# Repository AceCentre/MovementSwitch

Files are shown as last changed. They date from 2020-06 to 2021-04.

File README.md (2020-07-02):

# MovementSwitch

> Hardware project to make a very sensitive, self calibrating and auto-adjusting on-body switch

MovementSwitch is a Arduino project designed to work with a range of Arduino boards (e.g. Arduino Pro micro) and a GY-521 Gyroscope. The device self calibrates to a users movement and a potentiometer can be used to adjust the sensitivity. 



## Bill of materials

* x1 [Arduino Pro Micro](https://store.arduino.cc/arduino-micro)
* x1 [Gy-521 Gyroscope-Accelerometer](https://www.amazon.co.uk/WayinTop-MPU-6050-Gyroscope-Accelerometer-Converter/dp/B07P5YXBXV/)
* x1 [10K Pot](https://shop.pimoroni.com/products/pt10lv-horizontal-trimmer-multiple-values)
* x1 [Momentary Pushbutton or switch](https://shop.pimoroni.com/products/momentary-pushbutton-switch-12mm-square)

## Arduino wiring

* **Pin** 4 - Switch/Pushbutton **State**: Active Low 
* **Pin** A0 - Potentiometer	**State**: Active Low 
* **Pin** 5 - Switch Output/Relay	**State**: Active Low 
* **Pin** 3 -  SCL of GY-521
* **Pin** 2 -  SDA of GY-521
* **Pin** 7 -  INT of GY-521
* **Pin** 9 -  Neopixel

See also this [TinyCad Diagram](https://github.com/AceCentre/MovementSwitch/blob/master/MovementSwitchSCM.dsn) :

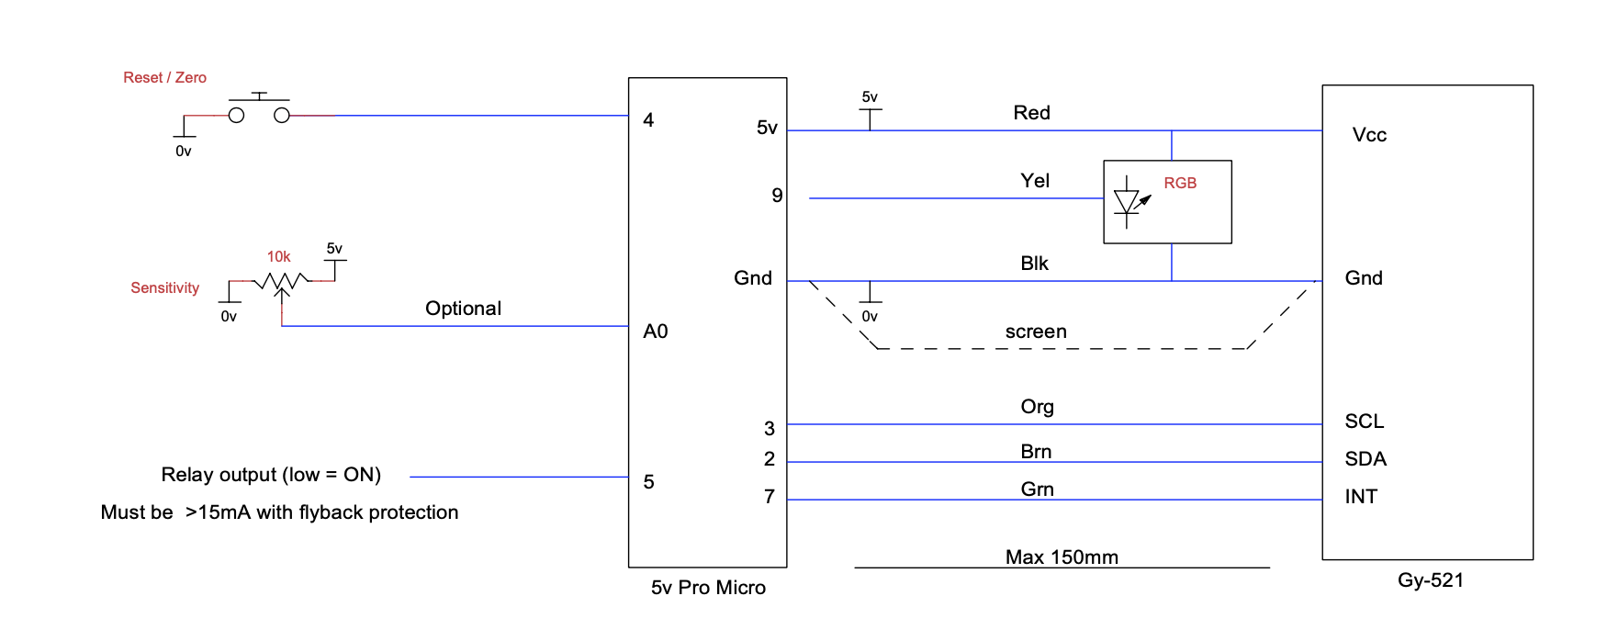
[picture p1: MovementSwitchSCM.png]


### Usage

Wire it all up. The neopixel displays different colours:

* **RED**: On first start for a few seconds as device calibrates. Wait with steady hand until complete
* **White**: OFF. Waiting to detect movement down* (up is an option)
* **Green**: ON A single keyboard character* will have been sent to the PC Now waiting to detect movement up*
* **Yellow**: OFF. Indicates that the user has managed to return further than original OFF position by a factor of 2. Consider reducing Sensitivity

**Zero / Reset Button:**

On press a fast zero will occur and the led will be Purple for a second or less then return to White indicating OFF

If the unit has had a major movement (dropped etc) and a quick reset is not possible, then the display will colour Red and commence a full reset taking a few seconds in the same manner as starting up.

**Sensitivity Knob:**

Max sensitivity when fully clockwise

## Contributing
Pull requests are welcome. For major changes, please open an issue first to discuss what you would like to change.

## Files

All the Arduino code is in the sub-directory **MovementSwitch**

* MovementSwitch.ino - Main source code file
* A_Main.ino - Main Gyro State Machine
* B_Gyro_.ino - Gyro Read data functions
* F_MonitorLight.ino - Logging functions. "Light" because it is a lightweight version of a more complex version Graham uses in his projects

### Required libraries 

You will need **THREE** libraries in your Arduino library folder for this to work:

* [I2Cdevlib](https://github.com/jrowberg/i2cdevlib/tree/master/Arduino/I2Cdev) and the [I2Cdevlib-MPU6050](https://github.com/jrowberg/i2cdevlib/tree/master/Arduino/MPU6050) Library in your Library folder. 
* [Adafruit Neopixel](https://github.com/adafruit/Adafruit_NeoPixel) Library

## Documentation Development

We use [vuepress](http://vuepress.vuejs.org) for documentation 

```bash
yarn dev
yarn build
```

## Credits

* Graham Law - Check out <http://celticmagic.org> for some great AT hardware. Graham wrote *ALL* of this code. Graham is a legend. Hire him! [See his page here which documents it from his side](https://www.celticmagic.org/movement-detector). 
* Gerard Cullen <http://www.rhn.org.uk> - Original inspiration and version 1 of this project was down to Gerard

## License
[MIT](https://choosealicense.com/licenses/mit/)

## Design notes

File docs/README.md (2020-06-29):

---
home: true
heroImage: https://v1.vuepress.vuejs.org/hero.png
tagline: Hardware project to make a very sensitive, self calibrating and auto-adjusting on-body switch
actionText: Quick Start →
actionLink: /guide/
features:
- title: Feature 1 Title
  details: Feature 1 Description
- title: Feature 2 Title
  details: Feature 2 Description
- title: Feature 3 Title
  details: Feature 3 Description
footer: Made by Will Wade with ❤️
---

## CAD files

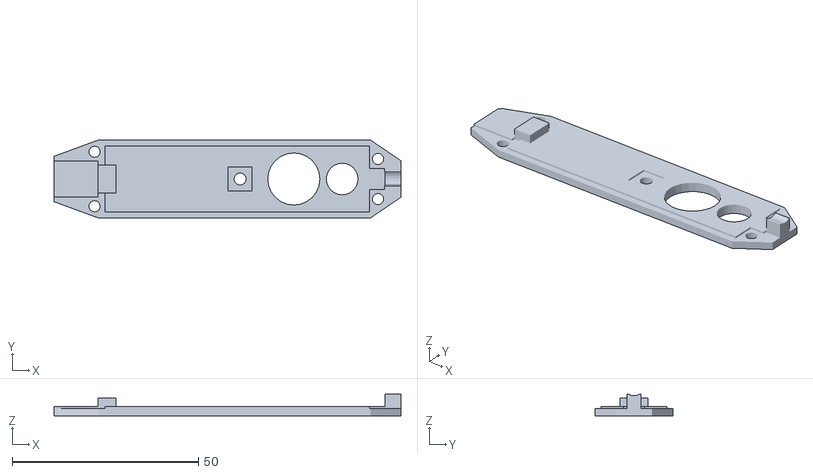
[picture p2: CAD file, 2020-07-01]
hardware/3D printing/ACE CoffinLid.stl
93.2 x 21.0 x 5.82

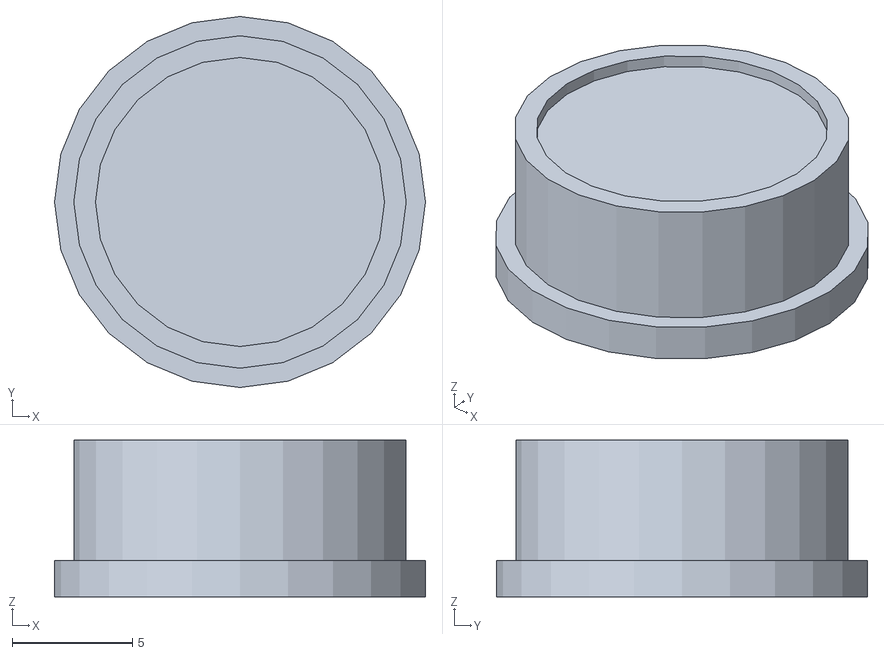
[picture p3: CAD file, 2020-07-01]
hardware/3D printing/ACE CoffinButton.stl
15.4 x 15.4 x 6.50

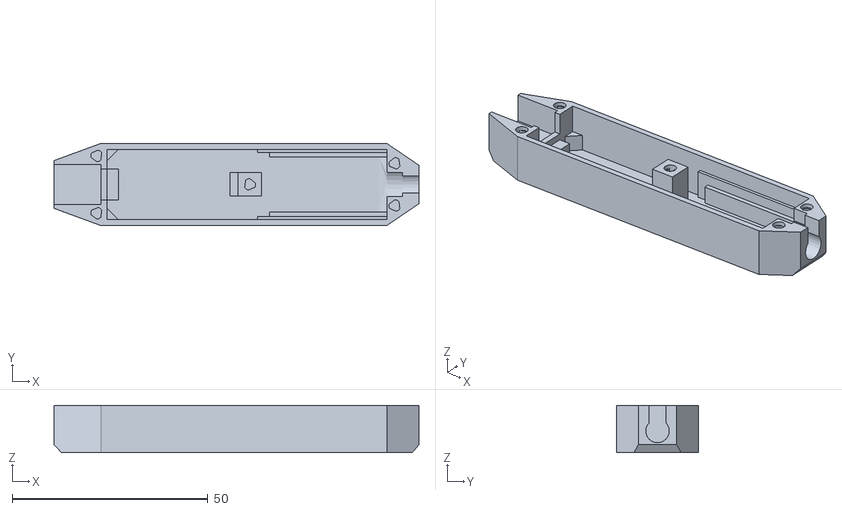
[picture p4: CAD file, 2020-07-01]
hardware/3D printing/ACE CoffinCase.stl
93.2 x 21.0 x 12.0

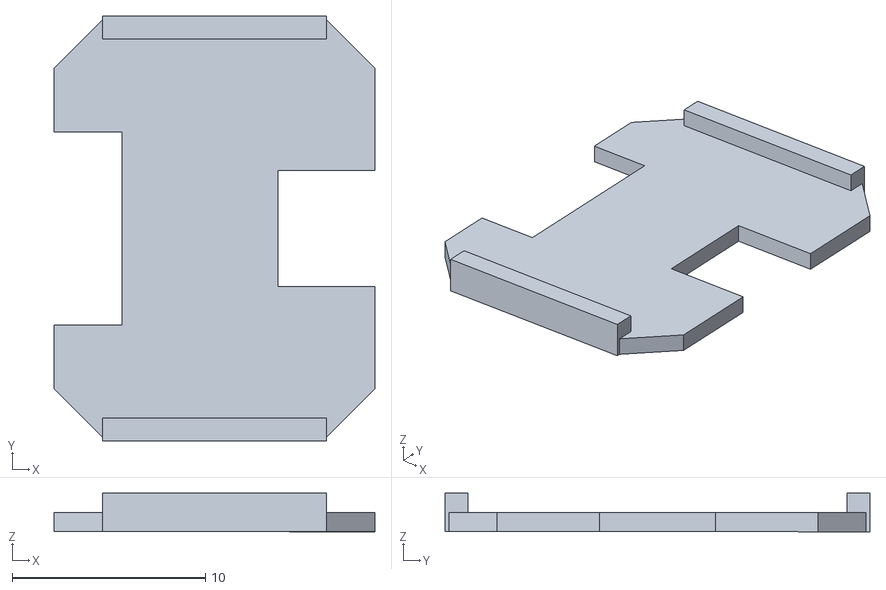
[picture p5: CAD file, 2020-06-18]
hardware/3D printing/ACE spacer.stl
16.6 x 22.0 x 2.00

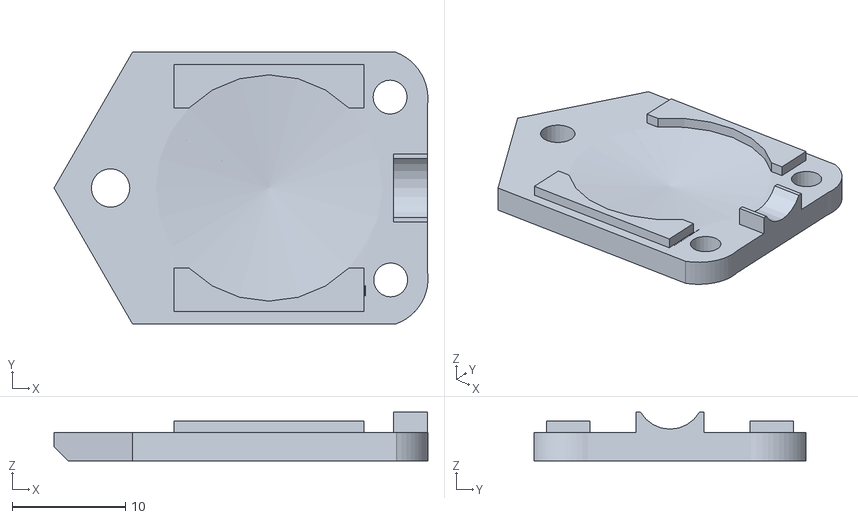
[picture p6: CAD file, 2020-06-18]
hardware/3D printing/ACE lens.stl
33.1 x 24.0 x 4.30

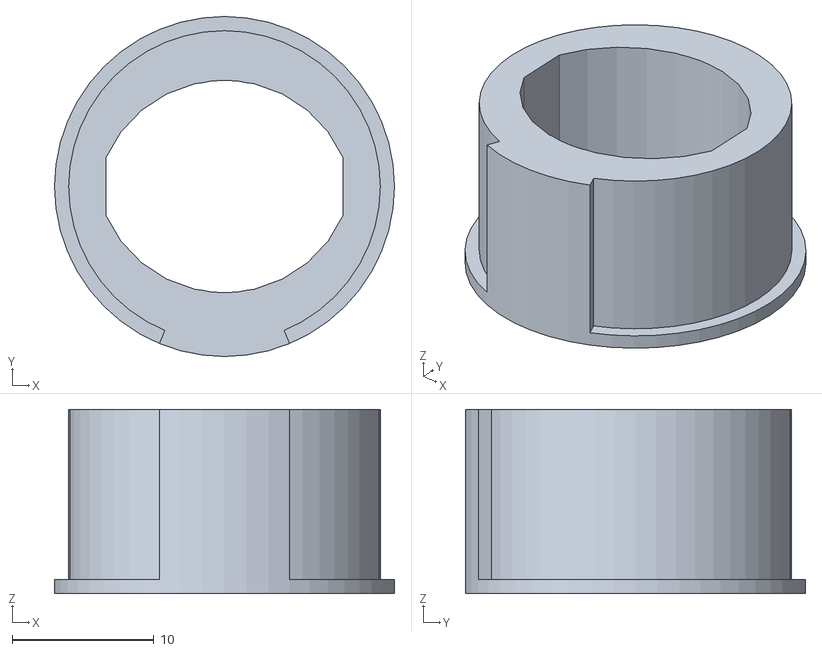
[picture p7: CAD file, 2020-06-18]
hardware/3D printing/ACE finger adaptor M .stl
24.0 x 24.0 x 13.0

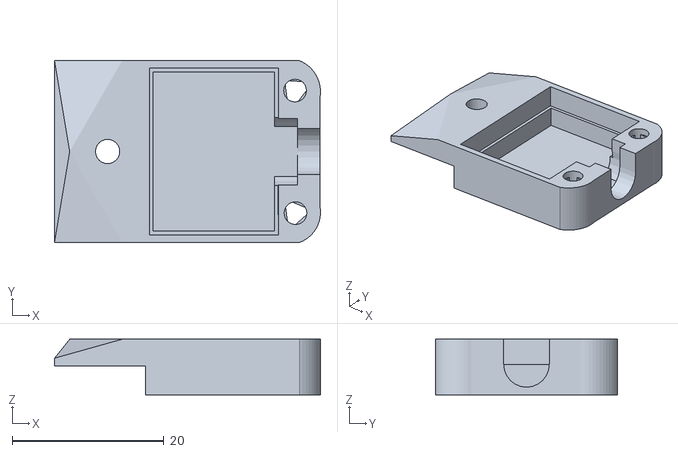
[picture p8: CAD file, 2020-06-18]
hardware/3D printing/ACE Case.stl
35.1 x 24.0 x 7.32

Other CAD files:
hardware/3D printing/ACE finger adaptor.stl
hardware/3D printing/ACE finger adaptor L .stl
hardware/3D printing/ACE finger adaptor S.stl
hardware/3D printing/ACE Case.skp

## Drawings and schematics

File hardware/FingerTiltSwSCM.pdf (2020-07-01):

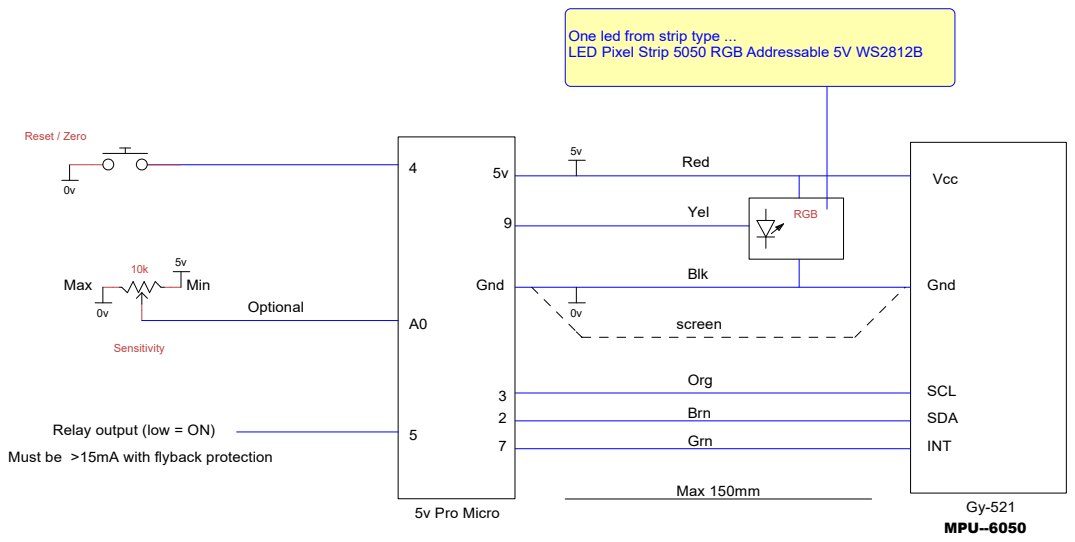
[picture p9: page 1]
Gnd; Vcc; 7 INT; SCL; 2 SDA; 5v Pro Micro; Sensitivity; RGB; Optional; Grn; Brn; Org; Red; Blk; Yel; Reset / Zero Relay output (low = ON); screen Max 150mm; MPU--6050; Max; Min

One led from strip type ...
LED Pixel Strip 5050 RGB Addressable 5V WS2812B

Must be >15mA with flyback protection

Title
Finger tilt switch
Author
GCL
Celtic Magic

File D:\Google Drive Stora ... FingerTiltSwSCM.dsn | Document SCM20052

Revision 0.1 | Date 15/6/20 | Sheets 1

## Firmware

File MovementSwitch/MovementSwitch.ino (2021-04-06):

     /*
Version:      1.2  29/7/20

1.2   FIXED  2D not reliably recalled after power up if in User mode


Open Source License - please leave this header intact.

Project:      Movement Detector based on the MPU650 Gyro
Originator:   Celtic Magic     www.celticmagic.org
Sponsored by: ACE Centre UK

Credits:
Thanks and credit given to Gyro  Libraries from Jeff Rowberg & the Arduino community.
Based on InvenSense MPU-6050 register map document rev. 2.0, 5/19/2011 (RM-MPU-6000A-00)
8/24/2011 by Jeff Rowberg <jeff@rowberg.net>

Legal bit:
THIS SOFTWARE IS PROVIDED BY THE COPYRIGHT HOLDERS AND CONTRIBUTORS "AS IS"
AND ANY EXPRESS OR IMPLIED WARRANTIES, INCLUDING, BUT NOT LIMITED TO, THE
IMPLIED WARRANTIES OF MERCHANTABILITY AND FITNESS FOR A PARTICULAR PURPOSE
ARE DISCLAIMED. IN NO EVENT SHALL THE COPYRIGHT HOLDER OR CONTRIBUTORS BE
LIABLE FOR ANY DIRECT, INDIRECT, INCIDENTAL, SPECIAL, EXEMPLARY, OR
CONSEQUENTIAL DAMAGES (INCLUDING, BUT NOT LIMITED TO, PROCUREMENT OF
SUBSTITUTE GOODS OR SERVICES; LOSS OF USE, DATA, OR PROFITS; OR BUSINESS
INTERRUPTION) HOWEVER CAUSED AND ON ANY THEORY OF LIABILITY, WHETHER IN
CONTRACT, STRICT LIABILITY, OR TORT (INCLUDING NEGLIGENCE OR OTHERWISE)
ARISING IN ANY WAY OUT OF THE USE OF THIS SOFTWARE, EVEN IF ADVISED OF THE    
POSSIBILITY OF SUCH DAMAGE.
*/   

//*******************************************************************************************************************
//***************  User Config      *********************************************************************************   
//*******************************************************************************************************************

  #define  DETECTION_STYLE_USER                      // _USER  Manual select 2D or 3D  
                                                     // _2D   fixed-  2D tilt normal    
                                                     // _2DR  fixed-  2D tilt reverse 
                                                     // _3D   fixed-  free space detection  
                                               
  #define  KEY_CHAR                      ' '         // Keyboard charecter when pressed - enter ASCII number for charector eg 97 = a     or enclose for same result ie 'a'      32 = Space
  #define  SENSITIVITY                     0         // 1-1000     if set to zero then sensitivity pot used from pin AD0
  #define  AUTO_CENTRE_RATE              0.2         // 0.1 - 1.0  this is how strong the auto centering works 
  

  #define  OVER_TRAVEL_OFF_COLOUR        YEL    
  #define  OFF_COLOUR                    WHT
  #define  ON_COLOUR                     GRN
  #define  OVER_TRAVEL_ON_COLOUR         GRN
  
    // valid colour codes     BLK,    RED,    GRN,    BLU,    YEL,    PUR,    CYN,  WHT,  WHTmax
    // Tip: if the Over Travel colours are not required then set them the same as the regular On / Off colours
    // Recommend that at least the OVER_TRAVLE_OFF_COLOUR is used as if consistently operating it suggests that the sensitivity can be set lower.


//       #define FLIP_POT_TRUE

  
// #define PRE_RELEASE_VERSION
//*******************************************************************************************************************
//***************  Libraries        *********************************************************************************
//*******************************************************************************************************************

#include "I2Cdev.h"
#include "MPU6050_6Axis_MotionApps20.h"
#include <math.h>
#include <EEPROM.h>
#include <Adafruit_NeoPixel.h>
#include "Keyboard.h"
MPU6050 mpu;


//*******************************************************************************************************************
//***************  System Constants *********************************************************************************
//*******************************************************************************************************************

  #define FALSE                    0
  #define TRUE                     1
  #define OFF                      0
  #define ON                       1
  #define NUL                     -1
  #define _10BIT                1024
  #define HALF_10BIT             512
  #define _8BIT                  255
  #define SPAN_8bit              255
  #define HALF_8BIT              127
  
  #define ROTATE                    0
  #define NOD                       1
  #define TILT                      2

  const long MPLEX_INTERVAL_xxMS  = 5;     
  enum {RUN_SM, RESET_SM, FULL_RESET_SM };
  enum {GYRO_NORMAL, GYRO_ZERO, GYRO_CAPTURE_POLARITIES, GYRO_LOAD_POLARITIES};
  enum {DETECT_STYLE_2D, DETECT_STYLE_2DR, DETECT_STYLE_3D };

//*******************************************************************************************************************
// System Global Variables  *****************************************************************************************
//*******************************************************************************************************************
  static long PreviousMillis        = 0;
  static int  tilt_output           = 0;
  static int  trig_threshold        = 0;
  static byte detection_style       = 0;
  static int  polarity_3d           = 1;
  static bool gyro_error            = FALSE;

//*******************************************************************************************************************
// MPU6050 Definitions     *****************************************************************************************
//*******************************************************************************************************************
  bool blinkState = false;
  // MPU control/status vars
  bool      dmpReady = false;  // set true if DMP init was successful
  uint8_t   mpuIntStatus;   // holds actual interrupt status byte from MPU
  uint8_t   devStatus;      // return status after each device operation (0 = success, !0 = error)
  uint16_t  packetSize;    // expected DMP packet size (default is 42 bytes)
  uint16_t  fifoCount;     // count of all bytes currently in FIFO
  uint8_t   fifoBuffer[64]; // FIFO storage buffer
  // orientation/motion vars
  Quaternion q;           // [w, x, y, z]         quaternion container
  VectorInt16 aa;         // [x, y, z]            accel sensor measurements
  VectorInt16 aaReal;     // [x, y, z]            gravity-free accel sensor measurements
  VectorInt16 aaWorld;    // [x, y, z]            world-frame accel sensor measurements
  VectorFloat gravity;    // [x, y, z]            gravity vector
  float euler[3];         // [psi, theta, phi]    Euler angle container
  float RNT[3];           // [yaw, pitch, roll]   yaw/pitch/roll container and gravity vector
  // packet structure for InvenSense teapot demo
  uint8_t teapotPacket[14] = { '$', 0x02, 0, 0, 0, 0, 0, 0, 0, 0, 0x00, 0x00, '\r', '\n' };


//*******************************************************************************************************************
// Hardware Definitions     *****************************************************************************************
//*******************************************************************************************************************

  #define RGB_LED_PIN     9
  #define PB_INPUT_PIN    4
  #define INTERRUPT_PIN   7  
  #define POT_AO_GAIN    A0
  #define NUM_PIXEL_LEDS  1
  #define RELAY_OUT       5
  
  Adafruit_NeoPixel strip = Adafruit_NeoPixel(NUM_PIXEL_LEDS, RGB_LED_PIN , NEO_GRB + NEO_KHZ800);


//*************************************************************************************************
// MONITOR LIGHT **********************************************************************************
//*************************************************************************************************

  //Shorthands
  #define  d0              di[0]
  #define  d1              di[1]
  #define  d2              di[2]
  #define  d3              di[3]
  #define  d4              di[4]
  #define  d5              di[5]
  #define  d6              di[6]
  #define  d7              di[7]
  
  #define DEB_ARRAY_SIZE  8
  static int di[DEB_ARRAY_SIZE];          // main debug array (ints)
  static int di_shadow[DEB_ARRAY_SIZE];




//*************************************************************************************************
// APP DATA       *********************************************************************************
//*************************************************************************************************


// LED colours
  #define NO_COLOURS 10
  #define BRIGHTNESS 100
  #define xb  *BRIGHTNESS)/100
  //                                     0       1       2       3       4       5       6       7       8     9
    enum                              { BLK,    RED,    GRN,    BLU,    YEL,    PUR,    CYN,    BLK2,   WHT,  WHTmax  };
    static const byte R[NO_COLOURS] = {(000 xb,(255 xb,(000 xb,(000 xb,(255 xb,(255 xb,(000 xb,(000 xb,(127 xb,(255 xb };
    static const byte G[NO_COLOURS] = {(000 xb,(000 xb,(255 xb,(000 xb,(255 xb,(000 xb,(255 xb,(000 xb,(127 xb,(255 xb };
    static const byte B[NO_COLOURS] = {(000 xb,(000 xb,(000 xb,(255 xb,(000 xb,(255 xb,(255 xb,(000 xb,(127 xb,(255 xb }; 
 


//*************************************************************************************************
// MAIN          **********************************************************************************
//*************************************************************************************************

void setup()
{
  F_MonitorLightInit(115200);
  HW_ConfigInit();
  B_Gyro_setup();
  Keyboard.begin();

#ifdef DETECTION_STYLE_2D 
  detection_style = DETECT_STYLE_2D;
#endif
#ifdef DETECTION_STYLE_2DR
  detection_style = DETECT_STYLE_2DR;
#endif
#ifdef DETECTION_STYLE_3D
  detection_style = DETECT_STYLE_3D;
#endif
#ifdef DETECTION_STYLE_USER
  while (B_UserModeChanger()); 
#endif
}


void loop()
{
  static byte  mplex_10ms = 0;
  unsigned long CurrentMillis;
  
  // FreeRunning Fast Stuff here *****
  B_Gyro_Interrupt_Processor();
  // Main Multiplexer Controller Tick 1mS intervals >>>>>>>>>>>>>>>>>>>>>>>>>>>
  CurrentMillis = millis();
  if (CurrentMillis - PreviousMillis > MPLEX_INTERVAL_xxMS)
   {
   PreviousMillis = CurrentMillis;
   mplex_10ms++;    // 0...4 for ever   
   if (mplex_10ms > 4)  { mplex_10ms = 0; }
   SM_10ms(mplex_10ms);
   }
}


// Mutiplexer - called every 10ms
//*************************************************************************

void SM_10ms(char mplex)
{
  A_Gryo_SM(RUN_SM);      //    <<<<<<<<<<<<<<<<< The Main Code runs here
  
  switch (mplex)
  {
    case 0:
      {
      F_MonitorLightRun();
      break;
      }
    case 1:
      {
      if (SENSITIVITY > 0)    { trig_threshold  = 1050 - SENSITIVITY; }               // use sensitivity value from header
#ifdef FLIP_POT_TRUE
        else                  { trig_threshold  = analogRead(POT_AO_GAIN) + 26; }     // or use A0 input
#else      
        else                  { trig_threshold  = 1050 - analogRead(POT_AO_GAIN); }   // or use A0 input
#endif      
      break;
      }
    case 2:
      {
      if (!digitalRead(PB_INPUT_PIN)) { A_Gryo_SM(RESET_SM); }    
      break;
      }
    case 3:
      {
      if (gyro_error) { gyro_error = FALSE;    A_Gryo_SM(FULL_RESET_SM); }
      break;
      }
    case 4:
      {
      // spare          
      break;
      }
  }
}


//*******************************************************************************************************************
// Interrupt detection       ****************************************************************************************
//*******************************************************************************************************************

volatile bool mpuInterrupt = false;     // indicates whether MPU interrupt pin has gone high
void dmpDataReady() 
 {
 mpuInterrupt = true;
 }
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

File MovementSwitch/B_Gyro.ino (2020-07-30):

// Tutorial on using the Gyro..,.
// https://www.mschoeffler.de/2017/10/05/tutorial-how-to-use-the-gy-521-module-mpu-6050-breakout-board-with-the-arduino-uno/



bool B_GyroRead(byte cmd)  
{
  if (detection_style == DETECT_STYLE_3D) { return GyroRead_3D(cmd); }      // split call to appriate function
  else                                    { return GyroRead_2D(cmd); }
}


//*******************************************************************************************************************
// Gyro 3D Processor     ****************************************************************************************
//*******************************************************************************************************************


bool GyroRead_3D(byte cmd)     // returns 0 if ok & 1 if problem
{
#define BASE_GAIN_3D     10000.0        // vector arithmetic results in longer diagonal vectors than 2D so compensate with reduced gain
#define PRIMARY_FILTER       0.05        // 0.001 -> 1.0 (off)
enum { RN,RT,NT };  
float  f1;
static float zero_offset_f[3]       = {0.0,0.0,0.0};
static float output_filtered_f[3]   = {0.0,0.0,0.0};
static float output_peak_f[3]       = {0.0,0.0,0.0};
static float base_gain_f[3]         = {BASE_GAIN_3D,BASE_GAIN_3D,BASE_GAIN_3D};
   
  mpu.dmpGetQuaternion        (&q, fifoBuffer);
  mpu.dmpGetGravity           (&gravity, &q);
  mpu.dmpGetYawPitchRoll      (RNT, &q, &gravity);

// Process data & auto centre
   for (int i=0; i < 3; i++)
    {
    f1 = base_gain_f[i] * RNT[i];                                                                                                // apply base gain with polarity
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

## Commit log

2020-06-18 inital import from Graham Law
    [ACE Case.skp, ACE Case.stl, ACE finger adaptor L .stl, ACE finger adaptor M .stl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]
2020-07-01 adding new stls
    [ACE Case.skp, ACE CoffinButton.stl, ACE CoffinCase.stl, ACE CoffinLid.stl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]
2020-07-30 adding changes from Graham - FIXED 2D not reliably recalled after power up if in User mode
    FIXED 2D not reliably recalled after power up if in User mode
